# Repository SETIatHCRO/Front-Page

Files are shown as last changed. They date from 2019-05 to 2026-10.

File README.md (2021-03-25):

# ata_docs
Documentation related to the Allen Telescope Array at the Hat Creek Radio Observatory in Hat Creek, California

Contents:

[**Analog-Signal-Components:**](Analog-Signal-Components) Documents relating to analog signal components

*Librarian: Alexander Pollak*

[**Antenna:**](Antenna) Documents relating to Antenna geometry and optical design

*Librarian: Alexander Pollak*

[**Antonio-Feed:**](Antonio-Feed) Documents related to V2 Antonio Feeds

*Librarian: Alexander Pollak*

[**Beamformer:**](Beamformer) Documents related to the first ATA beamformer

*Librarian: Billy Barott*

[**EMI:**](EMI) Documents related to site and device electromagnetic interference (EMI/RFI)

*Librarian: Janusz Kulpa*

[**HCRO-Network-Infrastructure:**](HCRO-Network-Infrastructure) Documents and drawings related to the HCRO ethernet infrastructure 

*Librarian: Alexander Pollak*

[**HCRO-Time-Standard:**](HCRO-Time-Standard) Documents and drawings related to the 1pps and 10MHz time distribution.

*Librarian: Alexander Pollak*

[**HVAC-Signal-Processing-Room:**](HVAC-Signal-Processing-Room) Documents and drawings related to the HVAC upgrade.

*Librarian: Alexander Pollak*

[**SITE:**](SITE) Documents related to the HCRO Site

*Librarian: Jon Richards*

[**SonATA:**](SonATA) Documents related to the SETI on ATA (SonATA) System

*Librarian: Jon Richards*

[**NOTES:**](NOTES) The NOTES stored on tumulus. General operating procedures.

*Librarian: Jon Richards*

[**Network:**](Network) Documents and drawings related to network and computer access..

*Librarian: Jon Richards*

Go to the [-> head over to wiki](https://github.com/SETIatHCRO/ata_docs/wiki)

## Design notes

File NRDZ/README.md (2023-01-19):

This directory contains material and links for the NRDZ activities at HCRO.

[TARDyS4 Overleaf](https://www.overleaf.com/2563835296ydvcvszfkjnm)

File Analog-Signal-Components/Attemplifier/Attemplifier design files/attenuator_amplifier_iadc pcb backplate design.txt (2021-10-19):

FYI: https://webfiles.berkeley.edu/obm/public_html/digibee_plate2.pdf

---------------------------- Original Message ----------------------------
Subject: attenuator/amplifier/iadc  pcb backplate design
From:    "Oren Milgrome" <obm@berkeley.edu>
Date:    Tue, November 6, 2007 5:03 pm
To:      davidm@astro.berkeley.edu
         urry@astro.berkeley.edu
         melvyn.wright@gmail.com
         mdexter@calmail.berkeley.edu
Cc:      danw@milkyway.ssl.berkeley.edu
         hchen05@ssl.berkeley.edu
         welch@astro.berkeley.edu
         barottw@erau.edu
--------------------------------------------------------------------------

Hi, check out the quick sketch of a iBOB 2x2 channel ADC with 4 channel 6
bit attenuator/amplifier pcb backplate design:

https://webfiles.berkeley.edu/obm/public_html/digibee_plate2.pdf

We would connect the amplifiers to the ADCs with short cables and edge
mount sma connectors. The indvidual channels will be shielded with the
same can foil as the filter boards.

Sincerely, Oren
>
> I think extension idea is OK.
> I recommend we design the extension so as to avoid the upper and lower
> card guides.  I think the alignment for smooth install/remove would be
> too hard to get so maybe better to just avoid altogether.
> At first glance I don't think this imposes too many restrictions.
>
>
> On Tue, 6 Nov 2007, Oren Milgrome wrote:
>
>> Hi, I'll draw it up as a 4" plate extension holding a 3x?" 4 channel
>> attenplifer pcb. Is the length overhange ok? Looks like a plan.
>> Thanks, Oren
>> > Yep.
>> >
>> > Maybe having lots of spares would help in the sense that we could
>> > drill extra holes and such into "spare" plate and then just dismount
>> the
>> > iBob+2ADC from existing plate, mount to new super-plate and then
>> reinstall
>> > into chassis.  This would minimize the disruption at HCRO.
>> >
>> > Many spare plates are in the left filing cabinet in the office.
>> >
>> > Matt
>> >
>> > On Tue, 6 Nov 2007, Oren Milgrome wrote:
>> >
>> >> Hi, maybe we could make a extender for the back plate? We could add a
>> >> few
>> >> holes to the existing parts.
>> >> The 4 channel attenplifier pcb could mount to the extender plate, and
>> >> connect to ADC vis short smas? Regards, Oren
>> >>
>> >> > Oren,
>> >> >
>> >> > See attached.
>> >> > First round of ~10 boards were made by frontpanelexpress.com
>> >> > can download simple software to design and order.
>> >> >
>> >> > It's not that critical but for better or worse we do have a large
>> >> stock
>> >> > of  these plates.  probably have about 100 spare.
>> >> >
>> >> > Vendor: Protofab Inc.
>> >> >    Sheryl Eiberg
>> >> >    Assistant Project Manager
>> >> >    1310 Stub Road
>> >> >    Petaluma, CA 94954
>> >> >    707 782 9669
>> >> >
>> >> >                                                unit
>> >> > description                              QTY   price     price
>> >> >
>> >> > Digibee (iBob) aluminum plate            249  $19.21686  $4,785.00
>> >> > holes cut w/ water jet.
>> >> > then counter sunk on CNC machine.
>> >> >   9.1850" x 10.2750"
>> >> >   thickness 2.0 mm
>> >> >   corner radius 0.00"
>> >> >   material: aluminum
>> >> >   finish: alodine MIL-C-5541 Class 3
>> >> >   color: natural (clear to light yellow from alodine finish)
>> >> > 3 weeks.
>> >> >
>> >> >
>> >> > Matt
>> >> >
>> >> > On Tue, 6 Nov 2007, Oren Milgrome wrote:
>> >> >
>> >> >> Hi Matt, do you have any cad files or drawings for the IBOB/ADC
>> >> >> Backplates?
>> >> >> Maybe we could make new plates to hold the attenplifiers pcbs?
>> >> >>
>> >> >>
>> >> >>
>> >> >> --
>> >> >> Oren Milgrome
>> >> >> University of California - Berkeley
>> >> >> Radio Astronomy Lab 601 Campbell Hall
>> >> >> Berkeley, CA 94720-3411
>> >> >> mobile: 510 368 6857 office: 510 642 5509
>> >> >> lab: 510 642 0381 fax: 510 642 3411
>> >> >> email: obm@berkeley.edu
>> >> >>
>> >> >>
>> >>
>> >>
>> >> --
>> >> Oren Milgrome
>> >> University of California - Berkeley
>> >> Radio Astronomy Lab 601 Campbell Hall
>> >> Berkeley, CA 94720-3411
>> >> mobile: 510 368 6857 office: 510 642 5509
>> >> lab: 510 642 0381 fax: 510 642 3411
>> >> email: obm@berkeley.edu
>> >>
>> >>
>> >
>>
>>
>> --
>> Oren Milgrome
>> University of California - Berkeley
>> Radio Astronomy Lab 601 Campbell Hall
>> Berkeley, CA 94720-3411
>> mobile: 510 368 6857 office: 510 642 5509
>> lab: 510 642 0381 fax: 510 642 3411
>> email: obm@berkeley.edu
>>
>>
>

-- 
Oren Milgrome
University of California - Berkeley
Radio Astronomy Lab 601 Campbell Hall
Berkeley, CA 94720-3411
mobile: 510 368 6857 office: 510 642 5509
lab: 510 642 0381 fax: 510 642 3411
email: obm@berkeley.edu

-- 
Oren Milgrome
University of California - Berkeley
Radio Astronomy Lab 601 Campbell Hall
Berkeley, CA 94720-3411
mobile: 510 368 6857 office: 510 642 5509
lab: 510 642 0381 fax: 510 642 3411
email: obm@berkeley.edu

-- 
Oren Milgrome
University of California - Berkeley
Radio Astronomy Lab 601 Campbell Hall
Berkeley, CA 94720-3411
mobile: 510 368 6857 office: 510 642 5509
lab: 510 642 0381 fax: 510 642 3411
email: obm@berkeley.edu

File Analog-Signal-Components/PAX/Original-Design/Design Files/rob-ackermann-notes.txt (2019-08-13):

This is from an email dated October 01, 2009 by Rob Ackermann. It references images contained in this directory.

Jon Richards - August 13, 2019

**************

Attached PAX schematic image "pax-schematic.jpg" shows bits leaving microcontroller enter back attenuator shift-register at (A), leave at (B), and enter front attenuator shift-register at (C).  Also note that on/off bit (red circle) is associated with back attenuator shift-register.

Attached microcontroller source code image "set-pam-cmnd.png" shows first argument, back_atten, assigned to high byte of pam_data (green background highlight).  Second argument, front_atten, assigned to low byte of pam_data (blue background highlight).  On/off bit set in high byte, therefore, associated with back_atten (red background highlight).

Attached microcontroller source code image "set-pam-poll-data.png" shows setpam_data bits shifted from microcontroller to PAX shift-registers in order least significant bits (front attenuator) to most significant bits (yellow and orange background highlights).

Final image "pam-test-bench.jpg" shows PAM controller test bench setup with front and back attenuator bits represented by bar-graph LEDs

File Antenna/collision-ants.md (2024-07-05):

## <u> Collision Antennas </u>

### Background

The 3 collision trio antennas (3f, 3g, 3h) are located close enough to collide with each other given certain
orientations.  A JSDA service <i>CollisionServer</i> running on antcntl receives telemetry from these antennas
and judges whether each is should be allowed to move.

### Current Implementation

#### Drivebox motion enable/disable mechanism

The drivebox controls motor speeds through the Copley Accelnet servo amps by using the amp's velocity mode control.
The drivebox generates pulse trains for both az and el servo amps, and the amps translate this proportionally into the
desired motors speed.  The pulse train always has 50% duty cycle (it is not PWM).  These pulse trains are
generated by ip2022-based drivebox firmware's <i>TMR0</i> interrupt routine.

The drivebox firmware listens on <i>UDP</i> port 1519 for "pulse" packets, which is just a packet with the
payload >= 5 bytes containing `pulse` as those first 5 bytes.  With each pulse packet received, a counter is reset to 4,
and is decremented in the watchdog timer service routine which runs at 1 Hz.  The pulse train generator code returns
early when the counter value is > 0, effectively stopping pulse generation and thus motion immediately halts or cannot
started.  The implication of this is that should motion be judged externally by CollisionServer, the antenna may
continue to move for 3-4 seconds while the counter runs down.

There is only one "pulse" enable counter, and it controls both axes together.

#### Non-collision antenna behavior

For the non-collision antenna case, the controlbox continously sends the "pulse" UPD messages to the drivebox at 1 Hz,
so pulse-train generation and thus motion is always possible.

#### Telemetry and drive enable messaging

- `controlbox:encoder_thread()`:<br>Sends encoder readings at 10 Hz to `DishServer:Tracker:EncoderServer` at UDP localhost:1515

- `controlbox:wrappot_thread()`:<br>For collision ants, sends wrappot readings to `CollisionServer` at UDP antcntl:1515
at 1 Hz.  For non-collision ants, it sends `pulse` messages to the drivebox UDP port 1519 at 1 Hz.

- `EncoderServer:DatagramLoop()`:<br>Receives encoder reading messages on UDP port 1515

- `EncoderServer:azEncoderCollisionLoop()`:<br>Receives encoder reading messages on UDP port 1515, calculates az angle
and forwards az position to `CollisionServer` at UDP antcntl:1515

- `CollisionServer:RunReceiveThread()`:<br>Receives `wrappot` and `az` packets from the embedded EncoderServer on a
collision ant, processes and if judged ok, sends a `pulse` packet to that ant's controlbox UDP port 1517.

- `controlbox:drivebox_thread()`:<br>listens on UDP port 1517 for `pulse` messages from `CollisionServer`, essentially
forwarding them to the drivebox UDP port 1519.  

#### CollisionServer

<i>TODO</i>

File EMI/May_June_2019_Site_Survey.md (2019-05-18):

**A description of some proposed actions for site RFI/EMI Testing**

References:

NRAO Resources:

https://greenbankobservatory.org/science/gbt-observers/rfi-mitigation/

https://science.nrao.edu/facilities/vla/docs/manuals/obsguide/rfi

https://www.cv.nrao.edu/~hliszt/RFI/RFI.htm

https://science.nrao.edu/facilities/gbt/interference-protection/ipg

BRAND-EVN:

https://radiowiki.mpifr-bonn.mpg.de/lib/exe/fetch.php?media=jra:730562_radionet-del6.1_170630.pdf
(Appendix 1, Page 10)

Also see there test setup description at http://www1.oan.es/reports/doc/IT-CDT-2017-13.pdf and http://www1.oan.es/reports/doc/IT-CDT-2016-16.pdf

Report on anechoic chamber tests of a ROACH II (for discussion vis-a-vis Franklin’s report on LaserSETI)

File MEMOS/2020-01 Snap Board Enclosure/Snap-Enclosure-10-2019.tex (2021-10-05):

\documentclass[12pt,a4paper,oneside]{article}
\usepackage[margin=1.2in]{geometry}
\usepackage{appendix}
\usepackage[dvips]{graphicx}
\usepackage{epsfig}
\usepackage{amsmath}
\usepackage{amssymb}
\usepackage{psfrag}
\usepackage[square, comma,sort,numbers]{natbib}
\usepackage{fancyhdr}
\usepackage[nottoc]{tocbibind}
\usepackage{color}
\usepackage{fixltx2e}
\usepackage{pdfpages}
\usepackage{pdflscape}
\usepackage{booktabs}
\usepackage{graphicx}
\usepackage{float}
\usepackage{afterpage}
\usepackage{subcaption}
\usepackage{lscape}
\usepackage{rotating}
\usepackage{enumitem}
\usepackage{array,tabularx}
\usepackage{fancyref}
\usepackage[dvipsnames]{xcolor}
\usepackage[colorlinks=true,allcolors=blue]{hyperref}%

\newcommand{\quotes}[1]{``#1''}

\newenvironment{conditions*}
  {\par\vspace{\abovedisplayskip}\noindent
   \tabularx{\columnwidth}{>{$}l<{$} @{\ : } >{\raggedright\arraybackslash}X}}
  {\endtabularx\par\vspace{\belowdisplayskip}}

\pagestyle{fancy}
\title{\Huge Allen Telescope Array\\
\vspace{0.5cm}
Smart Network ADC Processor\\1U Enclosure\\
\vspace{0.5cm}
\normalsize \emph{}
\vspace{3.5cm}
\begin{center}
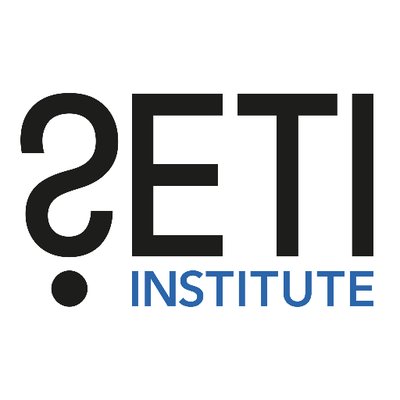
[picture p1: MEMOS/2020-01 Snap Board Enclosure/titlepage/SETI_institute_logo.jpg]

\end{center}
}
\author{ 
\vspace{1cm}
\Large
\textbf{ Alexander Pollak} \\
SETI Institute \\ 
189 Bernardo Ave, Suite 200 \\
Mountain View, CA 94043 \\ 
Alexander.Pollak.87@gmail.com\\
}
\date{\today}

\begin{document}
\clearpage\maketitle
\thispagestyle{empty}

%\newpage
%\thispagestyle{empty}
%\section*{Abstract}
%\noindent 
%

%
%\vspace{3cm}
%\begin{flushright}
%Alexander Pollak \\ \emph{September, 2015}
%\end{flushright}

%\newpage
%\thispagestyle{empty}
%\tableofcontents
\newpage

%----------------------------------------------------------------------------------------
%	SECTION 1
%----------------------------------------------------------------------------------------
%\pagestyle{plain}
\section{General}
\label{sec:1}
% ----------------------------------------------------------------

This document describes the design, component list, and assembly for a 1U SNAP Ver 2.1.1 MAR 2016 enclosure. The design is based on standard components and only requires two modified parts, which can be ordered via Front Panel Express using the included design files. In addition to housing the SNAP board, this design also includes SMA connections to support the ADC 5G V2.0 or any other compatible extension cards. Note, that this enclosure is not EMI-RFI shielded!

%----------------------------------------------------------------------------------------
\section{CAD Design and Drawings}
\label{sec:2}
% ----------------------------------------------------------------
This section includes a description of the CAD design. The enclosure has been designed to support all signal, communication, and power connections from the front. As a result of this, there was not enough space to include cooling fans into the front panel as well. In order to still ensure adequate cooling of the SNAP board and the 5G ADC card, directional fans have been installed which create an airflow from the right-hand side to the left-hand side. This configuration allows the 1U cases to be mounted without any space in between units while still providing sufficient cooling.

An image of the CAD model is shown in Figure \ref{fig:CAD-model}. One can see the internal arrangement of the SNAP board, power supply, directional fans, and the Raspberry Pi 2 Model B. The two custom parts are the front panel and the base plate, both colored in blue. The lid of the enclosure, not shown in this Figure, is perforated to further increase cooling. The drawings for the front panel and base plate are attached at the end of this document.

%
\begin{figure}[H]
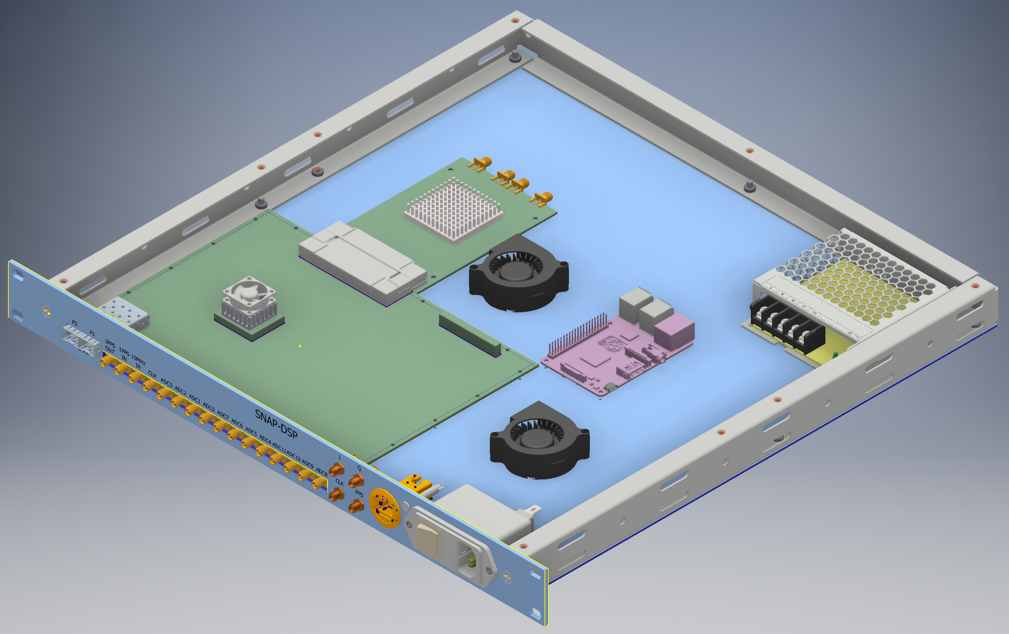
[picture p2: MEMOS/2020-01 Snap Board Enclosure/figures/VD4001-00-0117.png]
\centering{}
\caption{Schematic diagram of the measurement setup.}
\label{fig:CAD-model}
\end{figure}
%

\newpage

%----------------------------------------------------------------------------------------
\section{Component List}
\label{sec:3}
% ----------------------------------------------------------------
This section includes a list of the required components including their manufacturer and US distributer. The front panel and base plate can be ordered via {\color{blue} https://www.frontpanelexpress.com} by uploading the design files {\color{blue} VC4039-00-0001.fpd} and {\color{blue} VC4084-00-0018.fpd}. Not included are the SNAP board, 5G ADC card, and power supply cable from the PSU to the SNAP board. The total component cost for the enclosure is approximately 680\,USD.

\begin{table}[H]
\caption{Component List 1U SNAP Enclosure}
\resizebox{\textwidth}{!}{%
\begin{tabular}{@{}lllllll@{}}
\toprule
 Qty & Unit & Description                                              & Manufacturer             & PN Manufacturer & Distributor       & PN Distributer \\ \midrule
          &      &                                                          &                          &                             &                   &                             \\
1        & Each & LRS-75-12 -  POWER SUPPLY, AC-DC, 12V, 6A                	& Mean Well                		& LRS-75-12                   	& Newark            	& 44AC5561 \\
1        & Each & CHA-01-17, D-4001 1.75" Utility Chassis                  		& General Devices          		& CHA-01-17                   	& Quail Electronics 	& CHA-01-17 \\
1        & Each & Power Entry Module, Compact, IEC Inlet, 6A, 250VAC       	& SCHAFFNER                		& FN282-6-06                  	& Newark            	& 24M2150    \\
1        & Pack & Machine Screw, M3, 6 mm                                  			& TR FASTENINGS            	& M3 6 KRSTMC Z100	& Newark            	& 53M8781    \\
1        & Pack & SCREW, PAN HEAD PZ, M3, 4MM, 50PK                        	& DURATOOL                 		& DT000376                    	& Newark            	& 48AC6542  \\
1        & Pack & Machine Screw, M3, 25 mm                                 			& TRIPP-LITE         			& N001-S02-BL       		& Newark            	& 81Y0762  \\
1        & Each & Modular Connector, RJ45 Plug                             			& SCHNEIDER ELECTRIC       & XB5PRJ45                    	& Newark            	& 49AC2992  \\
1        & Each & Ethernet Cable, Cat5e, 600 mm, 2 ft                            		& SCHNEIDER ELECTRIC       & XB5PRJ45                    	& Newark            	& 49AC2992  \\
1        & Each & RPI2-MODB-V1.2                                           			& RASPBERRY-PI             	& RPI2-MODB-V1.2        	& Newark            	& 95Y1948    \\
1        & Each & GPIO Ribbon Cable for Raspberry Pi                       		& SAMTEC                   		& FFSD-20-D-04.00-01-N	& Newark            	& 99P5134    \\
1        & Each & ED Panel Mount Indicator, Green                          			& APEM                     		& Q6F3CXXG12E            	& Newark            	& 05W8310    \\
2        & Each & Fan Blower, GB Series, Compact, 12 V, DC                 		& SUNON                    		& GB1205PKV1-8AY.GN	& Newark            	& 96M8138     \\
18      & Each & SPACER, ROUND, POLYAMIDE, 4MM                           	& WURTH ELEKTRONIK         	& 960040010                  	& Newark            	& 94AC5835    \\
1        & Pack & SCREW, PAN HEAD PZ, M2, 8MM, 50PK                        	& DURATOOL                 		& DT000367                    	& Newark            	& 48AC6533      \\
1        & Pack & Washer, Plain, Brass, M2, Pack of 100                    		& DURATOOL                 		& M2 WASHER        		& Newark            	& 03P2386         \\
4        & Each & SMA Female to Female Adaptor Frequency: DC-6GHz          & Atlantic RF              		& SMA-1064 Rev A         	&                   &                             \\
4        & Each & Coaxial Cable Assemblies Standard Lengths - AFX Series   	& Atlantic RF              		& AFX-CA-141-24            	&                   &                             \\
1        & Each & Frontpanel                                               				& Front Panel Express, LLC 	& VC4039-00-0001.fpd     	&                   &                             \\
1        & Each & Base Plate                                               				& Front Panel Express, LLC 	& VC4084-00-0018.fpd    	&                   &                             \\
2        & Each & Fuse, Cartridge, Slow Blow, 2 A, 250 V                   		& Littlefuse               			& 0239002.HXP              	& Newark            	& 26K8412    \\
5        & Each & 8-32 X 3/8 STEEL ROUNDHEAD                               		& GC ELECTRONICS           	& KF-479                      	& Newark           	& 68R7355   \\
1        & Each & Barrier Terminal Block Connectors, Jumper, 38723 Series  	& MOLEX                    		& 38723-6502                  	& Newark            	& 72K2052    \\
7        & Each & Terminal, Locking, CLS Series, 22AWG to 18AWG, M3.5 	& MULTICOMP                		& CLS-TV-1806                 & Newark            	& 14T2409     \\ \bottomrule            
\end{tabular}}
\end{table}

%----------------------------------------------------------------------------------------
%	Power supply
%----------------------------------------------------------------------------------------
\section{Power Supply}
\label{sec:5}
% ----------------------------------------------------------------

The SNAP FPGA board and the cooling fans are supplied with a Mean Well 75\,W switch-mode PSU.
The unit is mounted directly to the base plate of the enclosure, thereby using the case as a thermal heatsink.
The operating temperature range of the PSU is from $-30^{\circ}$C through $70^{\circ}$C and the technical specifications are shown in Table \ref{tab:psu_spec}.
The power entry module, mounted in the front panel, combines an IEC inlet and a mains filter with a dual-fuse holder. The AC supply fuse current rating for this unit is selected to be 2\,A. 

\begin{table}[H]
\centering
\caption{Power Supply Specification}
\label{tab:psu_spec}
\begin{tabular}{@{}ccccc@{}}
\toprule
\multicolumn{1}{l}{Description} & \multicolumn{1}{l}{Output Voltage} & \multicolumn{1}{l}{Output Current} & \multicolumn{1}{l}{Power W} & \multicolumn{1}{l}{Input Voltage} \\ \midrule
LRS-75-12                         & 12\,VDC                               & 6A                               & 75W                         & $85 \sim 264\,\rm{VAC}$                              \\ \bottomrule
\end{tabular}
\end{table}

%----------------------------------------------------------------------------------------
%	Assembly
%----------------------------------------------------------------------------------------
\section{Assembled Unit}
\label{sec:6}
% ----------------------------------------------------------------
\begin{figure}[H]
\centering
   \begin{subfigure}[b]{1\textwidth}
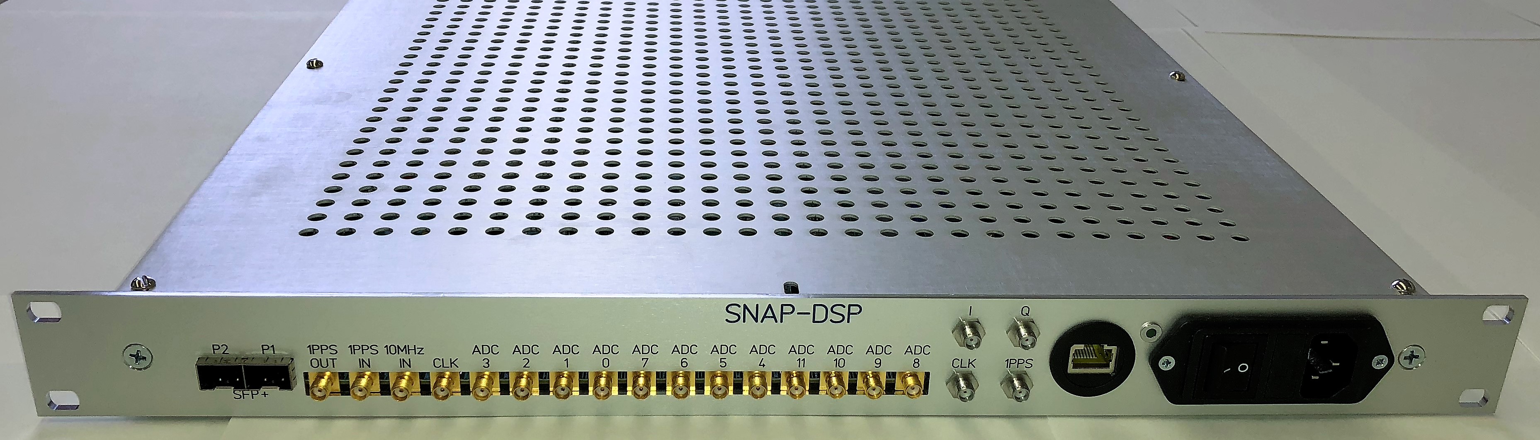
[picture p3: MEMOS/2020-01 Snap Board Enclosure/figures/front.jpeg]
   
   \caption{}
   \label{fig:front-view} 
\end{subfigure}
\begin{subfigure}[b]{1\textwidth}
	\vspace{1cm}
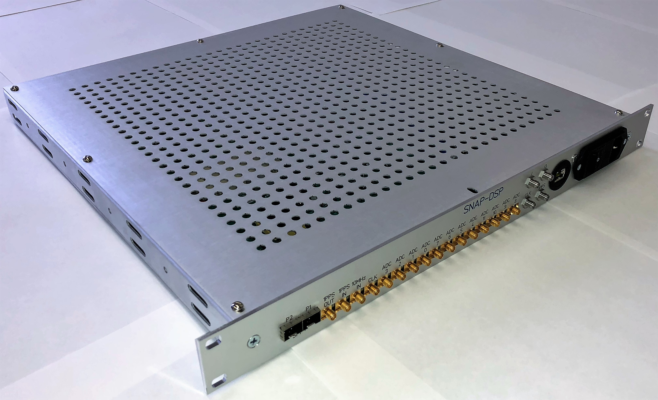
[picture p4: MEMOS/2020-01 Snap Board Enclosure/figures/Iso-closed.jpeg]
   
   \caption{}
   \label{fig:iso-view}
\end{subfigure}
\caption[Three numerical solutions]{Assembled 1U SNAP Enclosure; (a) Front view (b) Iso view.}
\label{fig:assembled-unit}
\end{figure}

%
\begin{figure}[H]
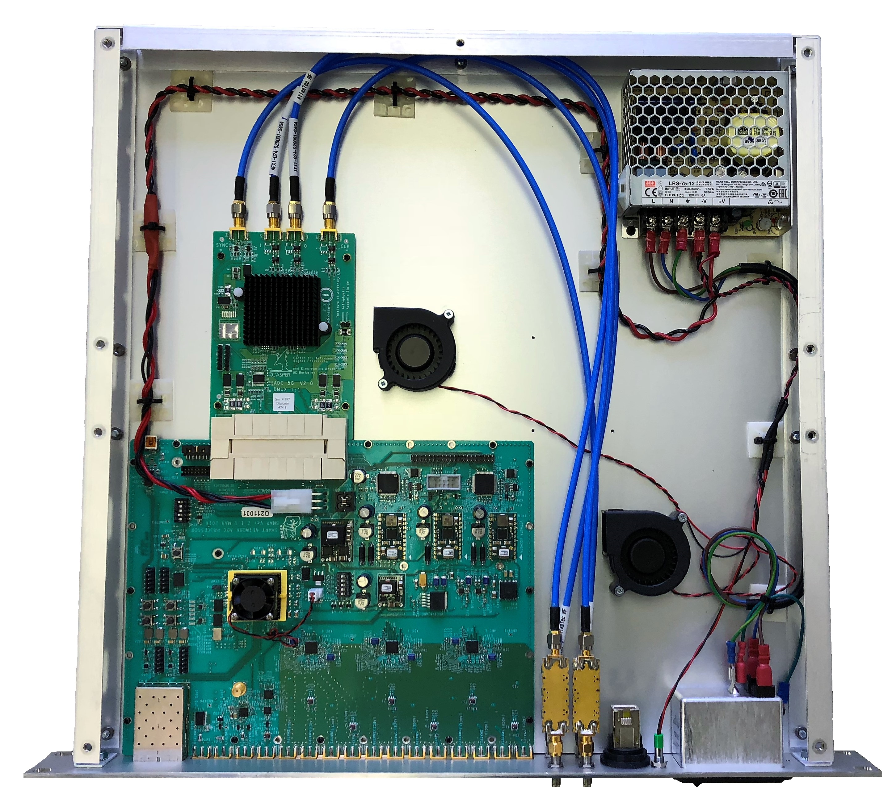
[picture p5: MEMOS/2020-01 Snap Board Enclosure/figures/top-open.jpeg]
\centering{}
\caption{Top view of the assembled case with the lid removed. Note that this unit has no Raspberry Pi installed.}
\label{fig:CAD-model}
\end{figure}
%

%----------------------------------------------------------------------------------------
%	APPENDIX
%----------------------------------------------------------------------------------------

\includepdf[pages={-},fitpaper,rotateoversize]{figures/VC4039-00-0001.pdf}
\label{DRAWING:VC4039-00-0001}
\includepdf[pages={-}, fitpaper,rotateoversize]{figures/VC4084-00-0018.pdf}
\label{DRAWING:VC4084-00-0018}

%----------------------------------------------------------------------------------------
%	BIBLIOGRAPHY
%----------------------------------------------------------------------------------------

%\bibliographystyle{apalike}
%\bibliographystyle{abbrv}

\bibliographystyle{apsrev}
\bibliography{bib_memos}

%----------------------------------------------------------------------------------------

\end{document}

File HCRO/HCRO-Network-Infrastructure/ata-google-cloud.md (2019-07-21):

ATA Data Google Cloud Storage
Jon Richards
SETI Institute
June 25, 2019

Introduction

This document explains details of the Google Cloud Storage used for ATA data. This includes the SQL database instance.

If you have any access issues, need access to the data buckets, etc., contact Jon Richards (jrichards@seti.org) and he will give you any access you want. You may wish to contact him first to make sure you should have access, before you get confused in the installation steps below.

For data storage the cloud is accessed using the gsutil utility provided by Google. There is a list of available commands:

•	Go to: https://cloud.google.com/storage/docs/gsutil_install
•	In the menu on the left igrate to gsutil tool -> gsutil Commands

Data Storage Bucket

The ATA data storage is located under the SETI-ATA Cloud project. The project name is “probable-cove-796”. It is in a bucket called ata_data. You access the files with the path “gs://ata_test_data”, once you have successfully completed “gcloud config” described below.

To view all the data directories in the probable-cove-796 project go to:

•	https://console.cloud.google.com/storage/browser/ata_test_data?project=probable-cove-796

The ata_test_data directory is under there; you can click to view all the files. 

Currently, the following ATA computers have access to this data configured and working, under the jrseti@gmail account:

•	NSG-head – this is the head node where the on/off data is stored in the /data directory.
•	sonata1 – this is the computer that contains the database and various utilities. The database on this computer is eventually going to be migrated to the cloud.
•	chan1x – this computer is used to read data from the beamformer, usually beam 1, x pol, and store it on a large disk mounted as “/data”. Relating to the cloud, the usual use case for this computer is to read and store beamformer data as it streams in (using hashpipe), convert the data to filterbank format, and push this data in the cloud. It is possible that some raw beamformer data  may be moved to the cloud, but it is so large and oppressive that hopefully storing raw beamformer data in the cloud will be a rare case.
•	chan2x – Same as “chan1x”, but for another beam or pol

SQL Database Instance

The SQL database instance stores all the feed sensor data. Grafana uses this instance as a data source. In theory anyone should be able to run his or her own Grafana server and use this SQL database instance as a data source.

The SQL database instance is at: 34.83.6.3, the database name is “ants”

To access read only, should work for anyone from any computer:

•	mysql --host=34.83.6.3--user=ata-sensors ants

Read/Write access is available if you connect from any computer originating from the ip address of the ATA, 70.100.31.22. Also, the user must be “ata-sensors-rw”.

•	mysql --host=34.83.6.3 --user=ata-sensors-rw ants

Utilities Installation
 
On your computer you need to do the following to access the data. Note that you will be using your own 

Install gsutil, follow the instructions at:

•	 https://cloud.google.com/storage/docs/gsutil_install

Once gsutil is installed, init your access to the gloud:

•	gcloud auth login --no-launch-browser (then follow directions)

Tell your computer which data bucket to use:

•	gcloud config set project probable-cove-796

You should now be able to access the data. Test that you can read a file from the gs://ata_data directory. There is a test file just for this purpose:

•	gsutil cp gs://ata_test_data/access_test_file.txt
•	Verify that access_test_file.txt transferred to your computer and you can view the simple text contents of the file.

Test your ability to write to the data directory, if you have write permissions. It may be the case you do not have write permissions if your use case is just to read data files. It is assumed that most users will not need or want write access, but if that is the case for you, test:

•	On your computer create a dummy file: “touch my_test.dat”
•	gsutil cp my_test.dat gs://ata_test_data
•	Go to https://console.cloud.google.com/storage/browser/ata_test_data?project=probable-cove-796
•	
•	View the list of files. You should see “my_test.dat” in the list. You may need to perform a refresh in your browser to see the data.
•	Remove the file: gsutil r mgs://ata_test_data/my_test.dat. Refresh the browser and confirm the file is removed.

Examples:

Rsync 6GB of files from /data/20190625 on NSG-head to gs://ata_test_data/rfi/:  

•	Do this in a screen!
•	cd /data
•	gsutil rsync -r 20190625 gs://ata

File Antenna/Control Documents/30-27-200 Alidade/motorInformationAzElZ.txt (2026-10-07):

Motor information:

PO#:12734.02PD 09/01/2005 [Incomplete] Cymatix MINEX
   011003: $53,909.00
	01	Qty: 47 ea  Az/El motor 
		"Part #AKM42J-EKMN2-03, Servo motor, 160VDC, 31.5 in-lb, 8.4 amp, 
		customized for IP20 plugs flying leads with J winding, 
		Housing 3.307 x 3.307 x 5.82, boss 2.875 x 0.118, pattern 0.218 on 3.875 circle, 
		shaft 0.500 x 1.250, key 0.125 x 0.750," 
		$475.00 /ea, $22,325.00 total

	02	Qty: 94 ea Az/El servo amplifier
		"Part #ACM-180-20-module, Servo amplifier, Accelnet module.180 VDC, 
		10 amp continuous, 20 amp peak." 
		$336.00 /ea $31,584.00 total
---------------------------------------------------------------------------------
(005:478) PO#:12774.03PD 09/01/2005 [Incomplete] Cymatix MINEX
   011003: $20,840.00
	01	Qty: 47 ea feed drive motor
		"Part #SN32HRYY-LNK-NS-00, Motor, AC Synchronous, Pacific Scientific, 
		NEMA 34, 3.38""sqr x 4.64 lg, 0.500""dia x 1.25""lg, 72 rpm, 480 0z-in running, 
		120VAC, 60 Hz, 1 Ph, flying leads (note: requires Resistor 200 ohm, 50w & requires Capacitor, 
		10uf x 370 Vac)" 
		$262.00 /ea $12,314.00 total

AKM42J-EKMN2-03
"AKM": AKM series
"4"  : motor frame size 4
"2"  : rotor stack length 2
"J"  : winding type J
"E"  : NEMA mount
"K"  : open keyway
"M"  : 0.5m shielded cable with IP20 plugs
"N"  : no brake
"2"  : 2048 PPR digital encoder w/ commutation
"03" : special shaft seal 03

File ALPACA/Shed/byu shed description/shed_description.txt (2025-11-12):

The sheds interior dimensions are 10' x 10' with an additional 4'3" x 2'5" x
5'10" nook in the back right corner for the comporessor. The interior floor to
ceiling dimension of BYU's shed is 8'.

ALPACA's dimenions when in the cart are described in:
'alpaca-cart-dimensions.png', 'ALPACA-clearnances.pdf', 'ALPACA-forklift
clearance.pdf'

The included drawings in, `ShedDrawings_July_2020.pdf` detail the shed's
construction, dimenions, and electrical specificaiton on pgs. 4-5. 

There are a few discrepancies from that drawing and what was built. It is best
to consider that document as a reference and what the building mateiral
specifications were. The signficant differences worth noting are:

  - The door is not center to the shed entrance. The door frame starts 18 inches
from the left and 36 inches from the right. This was to allow us to clear
the fenced area on BYU's roof and use the full range of motion in the cart to
tilt the array to the horizontal. This is shown in 'shed-door-dimensions.png'

  - A 4'3" x 2'5" x 5'10" nook for the comporessor in the back right corner.
The initial drawing shows the compressor outdoors, and did not include the
nook in the shed for the compressor. The space for the compressor was added
during construction of the shed with the change to instead store and run the
compressor from within the shed. We move the helium cables as needed when moving
the instrument in and out of the shed. Dimenions of this nook in the current
shed are shown in 'compressor_location.jpg'. A view of the compressor from the
outside is shown in "shed_side_compressor.jpeg" and
"shed_side_compressor_closed.jpeg".

Other current shed informaiton:

Door height has a clearance of 85" (shown in 'shed-door-dimensions.png')

The shed is insulated.

Included pictures show the rail dimensions and spacing as currently installed.
These rails we can remove from and ship with the instrument. Rails are shown in
'rails.jpeg'.

There are quad duplex NEMA 5-20R 120V outlet assemblies on each wall. The outlets are
4' off the ground on the back and side walls. The outlet on the 36" wall with the
door is 2' off the ground. We have four 20 A 120V circuits on our panel.

One 60A 480V 3 phase circuit for the compressor. The compressor is rated to
operate at 20A. More details about electrical operation of the compressor are in
the 'trillium-m700rt-helium-compressor-manual-c.pdf' on page 6.

Changes for at ATA:

- Increase the internal ceiling to floor height to at least 9' x 6". A 10'
  ceiling would add comfortable margin. This allows for replacing/removal of the
  top hat and servicing the array without taking the array outside. 

- Increase the door height by at least 3 inches

- Extend the shed to at least 2 to 3 feet in each dimension. As seen in the
  photos, there is enough room to work, but it is cramped. We also cannot
  service the instrument at the horizontal. Increasing the ceiling height and
  length will provide more space to conveniently service the array.

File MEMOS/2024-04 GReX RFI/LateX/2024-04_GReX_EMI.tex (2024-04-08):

\documentclass[12pt,a4paper,oneside]{article}
\usepackage[margin=1.2in]{geometry}
\usepackage{appendix}
\usepackage[dvips]{graphicx}
\usepackage{epsfig}
\usepackage{amsmath}
\usepackage{amssymb}
\usepackage{psfrag}
\usepackage[square, comma,sort,numbers]{natbib}
\usepackage{fancyhdr}
\usepackage[nottoc]{tocbibind}
\usepackage{color}
\usepackage{fixltx2e}
\usepackage{pdfpages}
\usepackage{pdflscape}
\usepackage{booktabs}
\usepackage{graphicx}
\usepackage{float}
\usepackage{afterpage}
\usepackage{subcaption}
\usepackage{lscape}
\usepackage{rotating}
\usepackage{enumitem}
\usepackage{array,tabularx}
\usepackage{fancyref}
%\usepackage[dvipsnames]{xcolor}
\usepackage[colorlinks=true,allcolors=blue]{hyperref}%
\usepackage[table,xcdraw]{xcolor}

\newcommand{\quotes}[1]{``#1''}

\newenvironment{conditions*}
  {\par\vspace{\abovedisplayskip}\noindent
   \tabularx{\columnwidth}{>{$}l<{$} @{\ : } >{\raggedright\arraybackslash}X}}
  {\endtabularx\par\vspace{\belowdisplayskip}}

\pagestyle{fancy}
\title{\Huge The Hat Creek Radio Observatory\\
\vspace{0.5cm}
GReX Electromagnetic Interference Measurements\\
\vspace{0.5cm}
\normalsize \emph{}
\vspace{3.5cm}
\begin{center}

\end{center}
}
\author{ 
\vspace{1cm}
\Large
\textbf{Alexander Pollak, Wael Farah, Marc Jacquart} \\
SETI Institute \\ 
339 Bernardo Ave, Suite 200 \\
Mountain View, CA 94043 \\ 
Alexander.Pollak.87@gmail.com\\
}
\date{\today}

\begin{document}
\clearpage\maketitle
\thispagestyle{empty}

\newpage

%----------------------------------------------------------------------------------------
%	General
%----------------------------------------------------------------------------------------

This document summarizes the testing of the GReX electronics' EM interferences at the Hat Creek Radio Observatory (HCRO) on April 3rd, 2024.

\section{Measurement setup}
\label{sec:Testing}

The GReX unit is place in the HCRO's screened room and it's electromagnetic emissions are recorded by a spectrum analyzer connected to an omnidirectional antenna through a signal amplifier. A schematic of the setup is shown in figure \ref{fig:measurement_setup_schematics}, a list of the components used in table \ref{tab:setup_component_list} and a picture of the setup inside the screened room is shown in figure \ref{fig:screened_room_setup}. A list of settings for the spectrum analyzer is shown in table \ref{tab:spectrum_analyzer_settings}. One modification was done for all the tests, compared to the state in which the GReX module was received: steel wool was added in the opening for the fiber cable to further shield the GReX enclosure.

A first baseline measurement was done with all the GReX electronics turned off. Then, the GReX was powered on and the emission spectrum was recorded for the GReX enclosure closed and opened separately. The SNAP board was programmed with the ``2023-08-16\_1325'' firmware after switching the unit on, but the 10 Gigabit Ethernet output was not enabled. As a final test, RF absorbers were placed in the GReX enclosure and the emission spectrum was once again measured with the enclosure closed. The hypothesis tested here is that the GReX enclosure acts as a resonant chamber for the EMI. Adding absorbers in the enclosure would reduce the interferences inside the enclosure, thus reducing the amount escaping the enclosure causing interferences on the outside.

\begin{figure}[H]
\centering
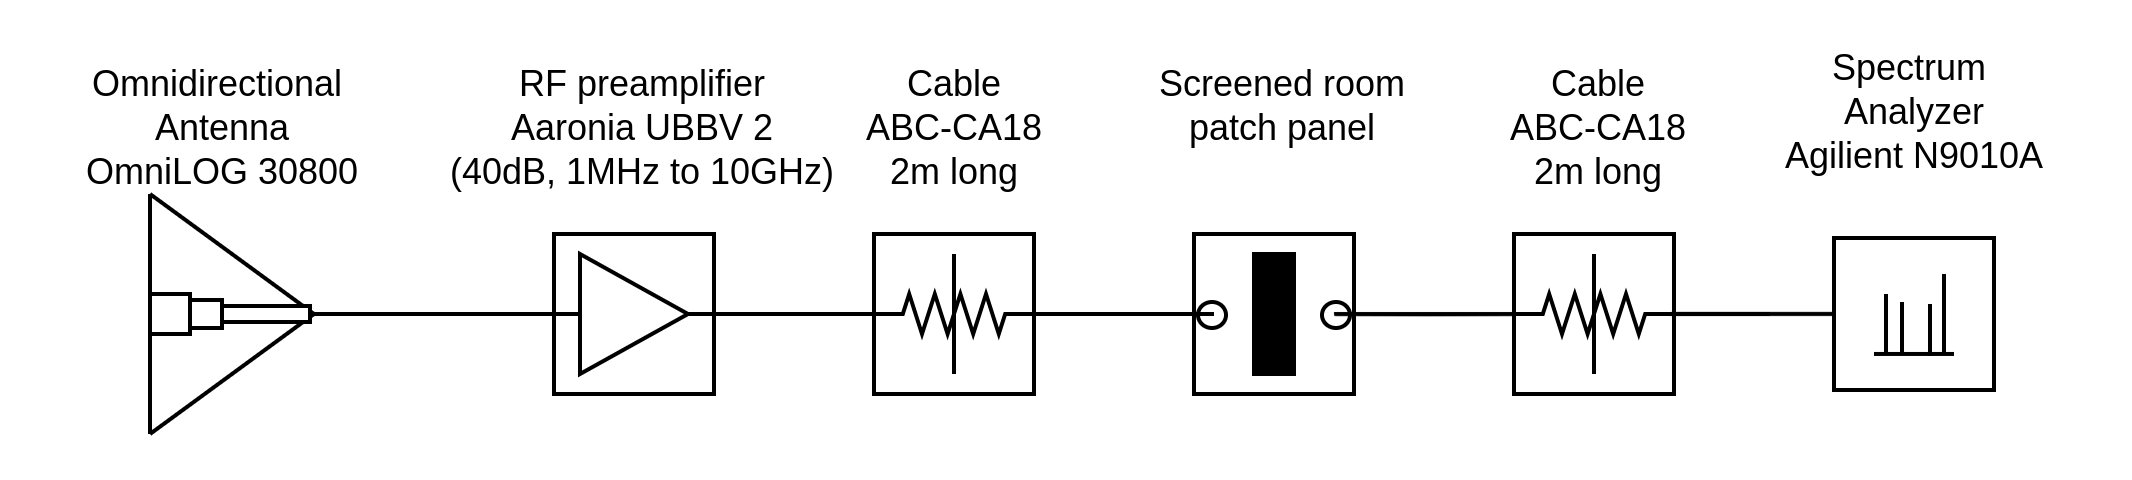
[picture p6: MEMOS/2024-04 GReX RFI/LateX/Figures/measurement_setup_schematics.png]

\caption{GReX EMI measurement setup schematics.}
\label{fig:measurement_setup_schematics}
\end{figure}
%
\begin{figure}[H]
\centering
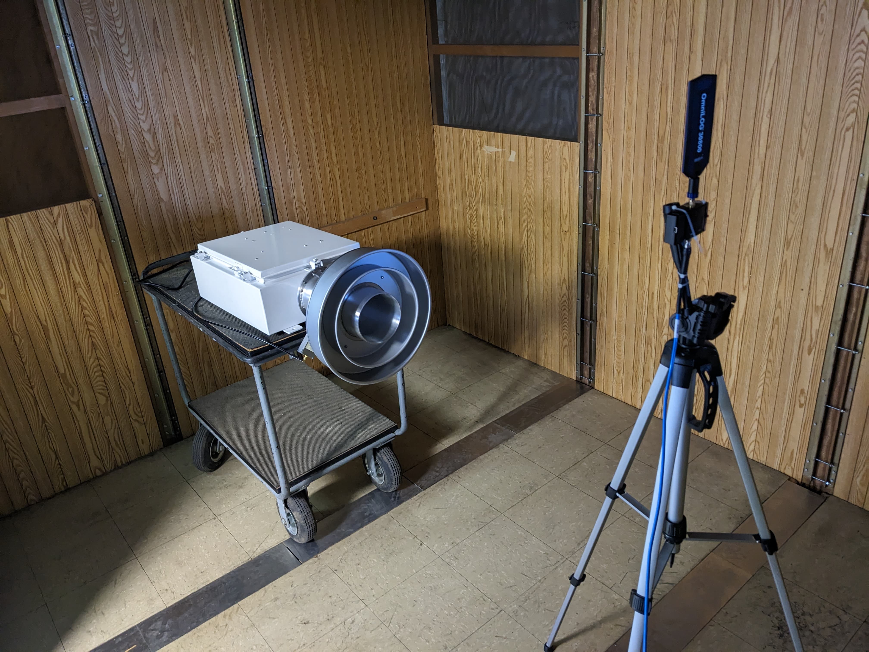
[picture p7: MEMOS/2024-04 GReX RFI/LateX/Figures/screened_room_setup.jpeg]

\caption{GReX EMI measurement setup in the HCRO screened room.}
\label{fig:screened_room_setup}
\end{figure}
%
\begin{table}[]
    \centering
   
    \begin{tabular}{|c|c|}
    \hline
         \cellcolor[gray]{0.85} Description & \cellcolor[gray]{0.85} Designation \\ \hline
         Omnidirectional antenna & OmniLOG 30800\\ \hline
         RF preamplifier & Aaronia UBBV 2\\ \hline
         Female-Female SMA cable 2m & ABC-CA18-SMSM-2.OM\\ \hline
         Female-Female SMA cable 5m & ABC-CA18-SMSM-5.OM\\ \hline
         Spectrum analyzer & Agilent N9010A\\ \hline
    \end{tabular}
    \caption{Components list for the GReX EMI measurements.}
    \label{tab:setup_component_list}
\end{table}

\begin{table}[]
    \centering
   
    \begin{tabular}{|c|c|}
    \hline
         \cellcolor[gray]{0.85} Description & \cellcolor[gray]{0.85} Setting \\ \hline
          Start Frequency & $300\thinspace$MHz \\ \hline
          Stop Frequency & $6\thinspace$GHz \\ \hline
          Number of points & 1001 \\ \hline
          Sweep time & 656.176 s\\ \hline
          RBW & $100\thinspace$Hz \\ \hline
          VBW & $1000\thinspace$Hz \\ \hline
          Attenuation & 0 dB\\ \hline
          Trace type & Maxhold \\ \hline
          Detector & Peak \\ \hline         
    \end{tabular}
    \caption{ Agilent N9010A specrum analyzer settings list for the GReX EMI measurements.}
    \label{tab:spectrum_analyzer_settings}
\end{table}
% ----------------------------------------------------------------
\section{Results}
\label{sec:Results}

The baseline spectrum is shown in figure \ref{fig:baseline_result}. The emission peaks around $1\thinspace$GHz are due to the EMI emitted by the spectrum analyzer itself, even though it is set outside the screened room for the measurements. However, this contribution is negligible compared to the GReX measurements shown below. Figure \ref{fig:open_result} shows the spectrum for the GReX enclosure open. The spectrum measurement result with the GReX enclosure closed is shown in figure \ref{fig:closed_result}. Finally, figure \ref{fig:absorber_comparison_spectrum} shows the effect of adding absorbers inside the enclosure. These four spectra are respectively referred below as ``baseline'', ``open'', ``closed'' and ``absorber''. A list of the highest interference peaks, defined as a value greater than $30\thinspace$dB above its neighbors and a distance of at least 5 spectrum values between each peaks, is reported in table \ref{tab:main_emission_peaks}.

\begin{figure}[H]
\centering
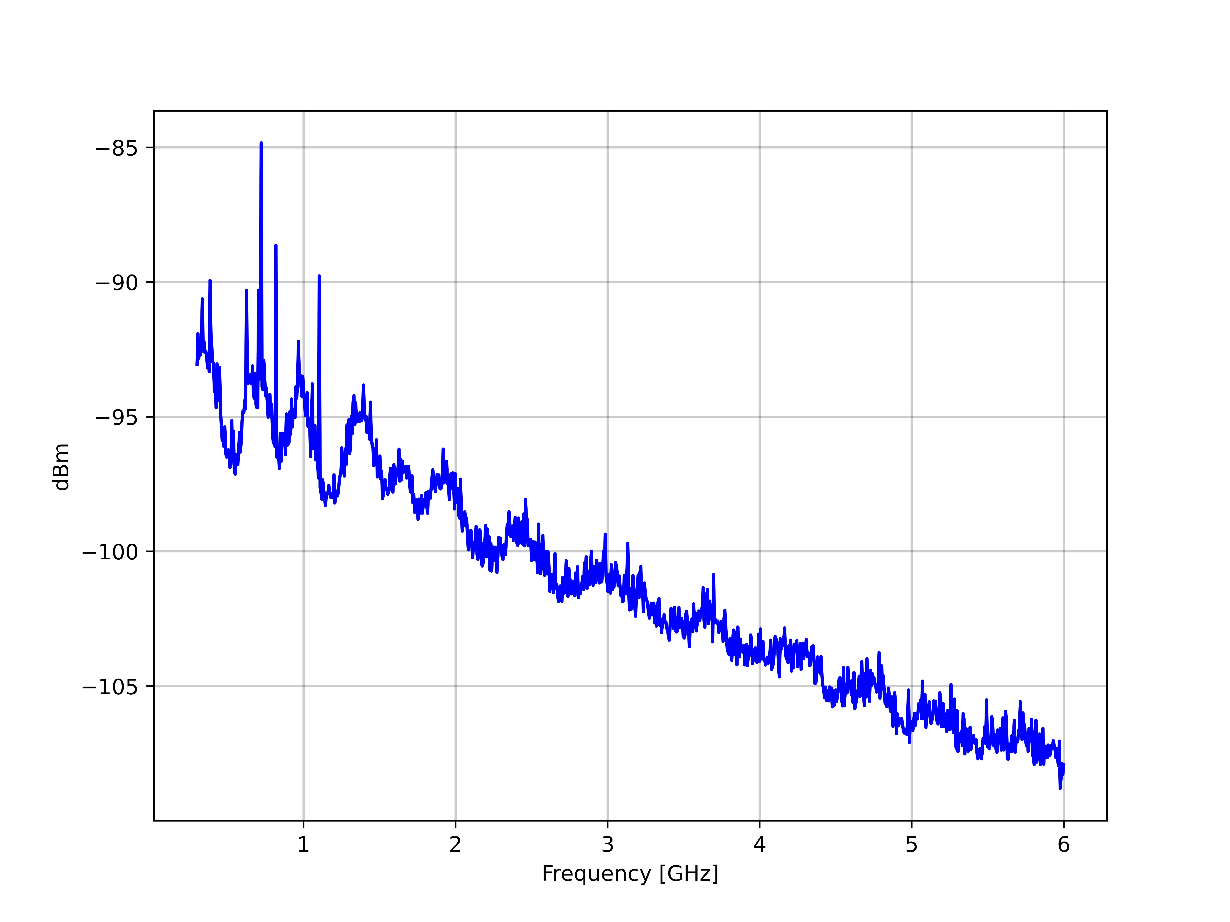
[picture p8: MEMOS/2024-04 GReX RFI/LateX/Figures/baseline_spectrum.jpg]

\caption{Baseline spectrum for the GReX EMI measurements.}
\label{fig:baseline_result}
\end{figure}
%
\begin{figure}[H]
\centering
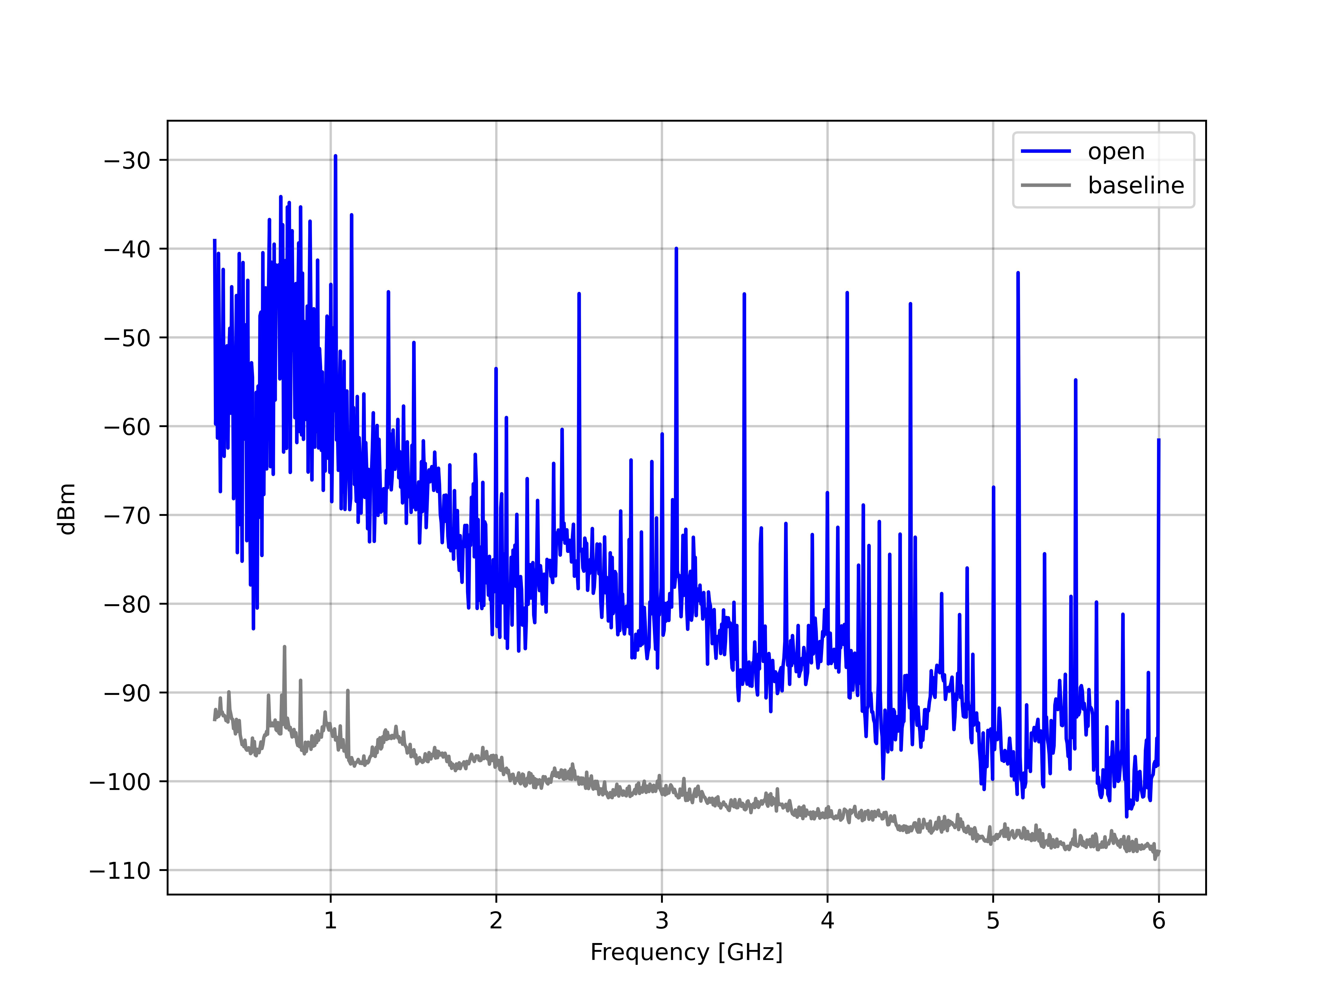
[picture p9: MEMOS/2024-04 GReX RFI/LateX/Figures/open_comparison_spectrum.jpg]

\caption{EMI emission spectrum of the GReX unit with its enclosure opened, compared with the baseline spectrum.}
\label{fig:open_result}
\end{figure}
%
\begin{figure}[H]
\centering
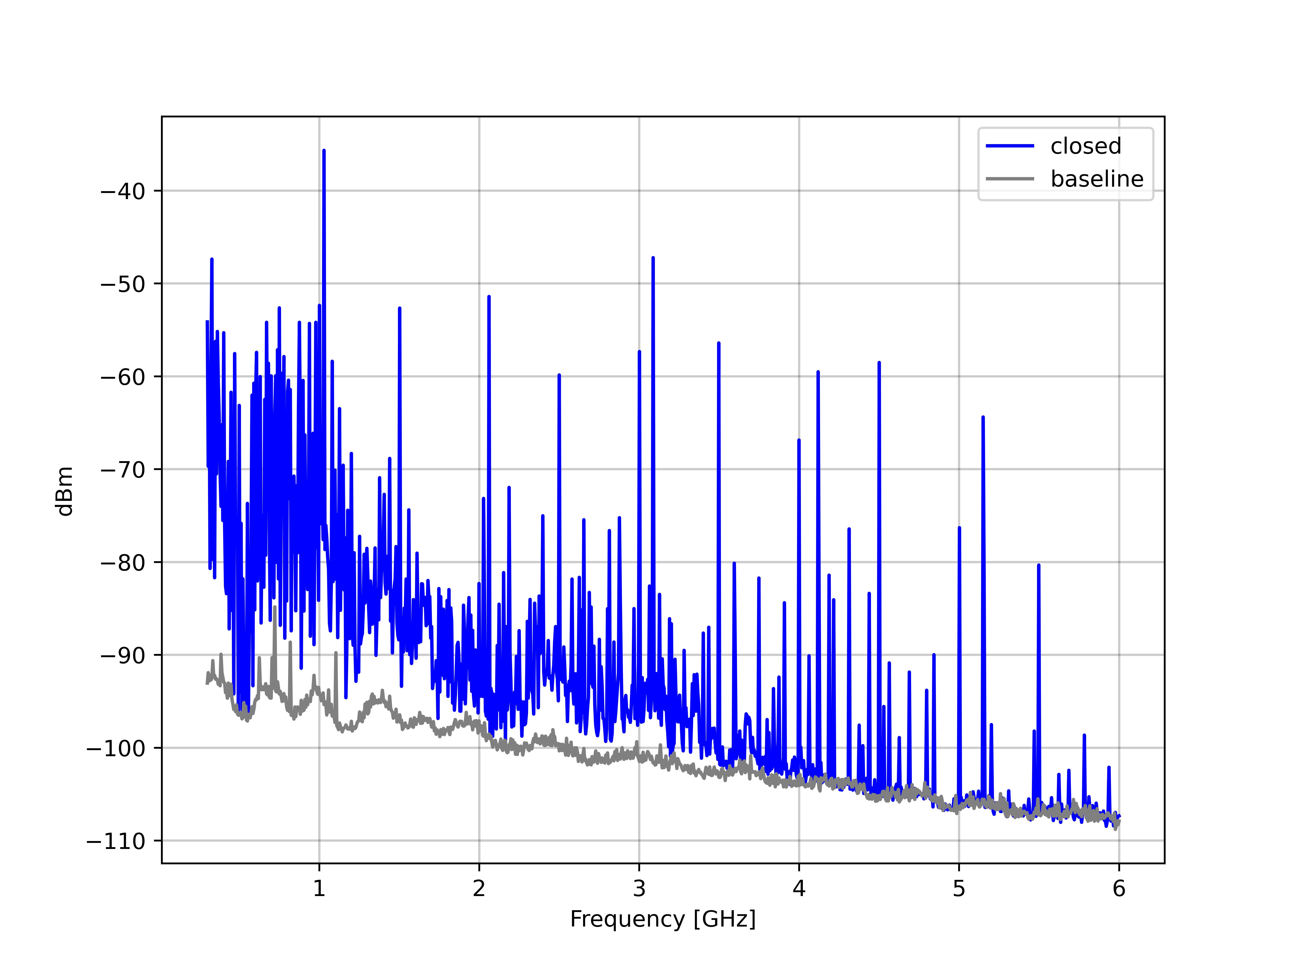
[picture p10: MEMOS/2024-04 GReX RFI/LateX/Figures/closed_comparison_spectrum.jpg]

\caption{EMI emission spectrum of the GReX unit with its enclosure closed, compared with the baseline spectrum.}
\label{fig:closed_result}
\end{figure}
%
\begin{figure}[H]
\centering
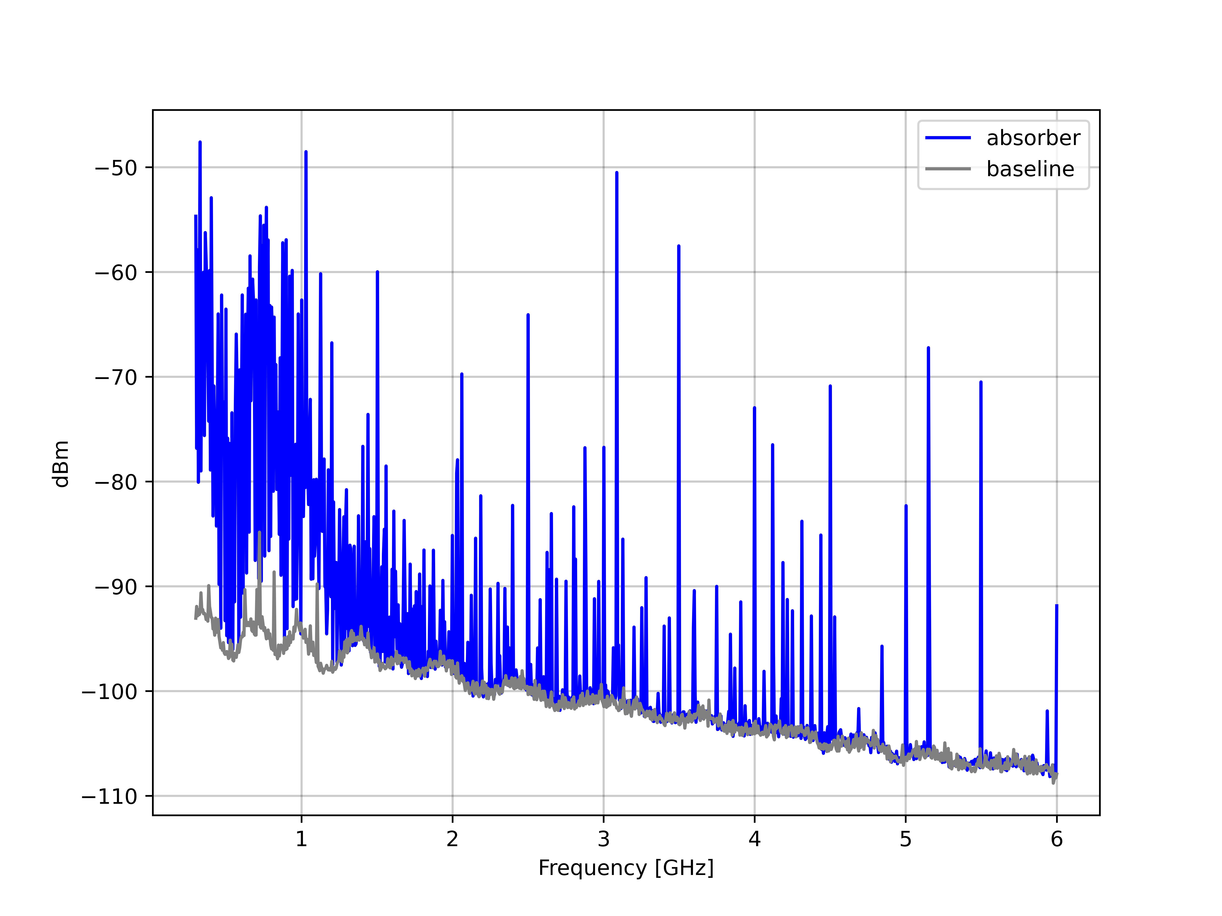
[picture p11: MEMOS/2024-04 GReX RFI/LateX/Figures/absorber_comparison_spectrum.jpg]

\caption{EMI emission spectrum of the GReX unit with its enclosure closed and absorbers added inside the enclosure, compared with the baseline spectrum.}
\label{fig:absorber_comparison_spectrum}
\end{figure}

\begin{table}[]
    \centering
   
    \begin{tabular}{|c|c|c|}
    \hline
         \cellcolor[gray]{0.85} Measurement & \cellcolor[gray]{0.85} Frequency [GHz] &  \cellcolor[gray]{0.85} Amplitude [dBm]\\ \hline
         open & 3.0873 & -39.978501 \\ \hline
         open & 3.4977 & -45.107806 \\ \hline
         open & 4.1190 & -44.959350 \\ \hline
         open & 4.5009 & -46.206643 \\ \hline
         open & 5.4984 & -54.792139 \\ \hline
         \hline
         closed & 0.4995 & -63.143009 \\ \hline
         closed & 1.0296 & -35.672183 \\ \hline
         closed & 1.5027 & -52.661033 \\ \hline
         closed & 2.0613 & -51.418850 \\ \hline
         closed & 2.5002 & -59.862832 \\ \hline
         closed & 3.0018 & -57.345924 \\ \hline
         closed & 3.0873 & -47.234282 \\ \hline
         closed & 3.4977 & -56.419926 \\ \hline
         closed & 3.9993 & -66.870435 \\ \hline
         closed & 4.5009 & -58.519204 \\ \hline
         \hline
         absorber & 1.0296 & -48.517166 \\ \hline
         absorber & 2.5002 & -64.079893 \\ \hline
         absorber & 3.0873 & -50.503989 \\ \hline
         absorber & 3.4977 & -57.511396 \\ \hline
         absorber & 3.9993 & -72.956611 \\ \hline
         absorber & 4.5009 & -70.879781 \\ \hline
         absorber & 5.4984 & -70.499525 \\ \hline

    \end{tabular}
    \caption{List of main emission peaks in the spectrum recorded for the GReX EMI measurements. Computed using scipy.signal's find\_peaks function (threshold: 30, distance: 5).}
    \label{tab:main_emission_peaks}
\end{table}

\end{document}

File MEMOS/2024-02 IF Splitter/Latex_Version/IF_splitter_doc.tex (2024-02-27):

\documentclass[12pt,a4paper,oneside]{article}
\usepackage[margin=1.2in]{geometry}
\usepackage{appendix}
\usepackage[dvips]{graphicx}
\usepackage{epsfig}
\usepackage{amsmath}
\usepackage{amssymb}
\usepackage{psfrag}
\usepackage[square, comma,sort,numbers]{natbib}
\usepackage{fancyhdr}
\usepackage[nottoc]{tocbibind}
\usepackage{color}
\usepackage{fixltx2e}
\usepackage{pdfpages}
\usepackage{pdflscape}
\usepackage{booktabs}
\usepackage{graphicx}
\usepackage{float}
\usepackage{afterpage}
\usepackage{subcaption}
\usepackage{lscape}
\usepackage{rotating}
\usepackage{enumitem}
\usepackage{array,tabularx}
\usepackage{fancyref}
\usepackage[dvipsnames]{xcolor}
\usepackage[colorlinks=true,allcolors=blue]{hyperref}%

\newcommand{\quotes}[1]{``#1''}

\newenvironment{conditions*}
  {\par\vspace{\abovedisplayskip}\noindent
   \tabularx{\columnwidth}{>{$}l<{$} @{\ : } >{\raggedright\arraybackslash}X}}
  {\endtabularx\par\vspace{\belowdisplayskip}}

\pagestyle{fancy}
\title{\Huge The Hat Creek Radio Observatory\\
\vspace{0.5cm}
The IF Splitter\\
\vspace{0.5cm}
\normalsize \emph{}
\vspace{3.5cm}
\begin{center}

\end{center}
}
\author{ 
\vspace{1cm}
\Large
\textbf{ Alexander Pollak \& Marc Jacquart} \\
SETI Institute \\ 
339 Bernardo Ave, Suite 200 \\
Mountain View, CA 94043 \\ 
Alexander.Pollak.87@gmail.com\\
}
\date{\today}

\begin{document}
\clearpage\maketitle
\thispagestyle{empty}

%\newpage
%\thispagestyle{empty}
%\section*{Abstract}
%\noindent 
%

%
%\vspace{3cm}
%\begin{flushright}
%Alexander Pollak \\ \emph{September, 2015}
%\end{flushright}

%\newpage
%\thispagestyle{empty}
%\tableofcontents
\newpage

%----------------------------------------------------------------------------------------
%	General
%----------------------------------------------------------------------------------------
%\pagestyle{plain}
\section{General}
\label{sec:General}
% ----------------------------------------------------------------

This document outlines general information regarding the IF Splitter such as the design, parts, wiring and testing. This information is aimed at detailing the entire process of creating an IF Splitter from design to manufacturing and testing. 

The purpose of the IF Splitter is to divide the incoming signal of one of the tuning (tuning "D" at the ATA) into three separate outputs. First, the signal is divided in two and one half goes directly to an output (3dB attenuation). The second output is divided in two again, leading to two more outputs with 6dB attenuation. This system allows to plug additional equipment (i.e. GNU radio, testing or monitoring devices) without unplugging the main data acquisition channel, making the ATA more polyvalent.

In this document, "IF splitter" designates the whole module while a "power splitter" designate the ZX10-2-12-S+ component that divides a signal in half. One IF splitter 6U module contains 96 power splitter components.
%----------------------------------------------------------------------------------------
%	CAD Design and Drawings
%--------------------------------------------------------------------------------------

\section{CAD Design and Drawings}
\label{sec:CAD}
% ----------------------------------------------------------------
This section includes a description of the CAD design. Figure \ref{fig:CAD_outside} shows the outside of the IF splitter module with the front panel containing the two groups of 6dB outputs. Figure \ref{fig:CAD_inside} shows the IF splitter module open, with the mounts and signal splitter components but no cable. The left CAD drawing shows the back panel with the group of inputs on top and the group of 3dB Outputs below. Both the front and back panel look similar in the number and placement of the SMA connectors. As a visual reference, it can be noted that the two handles are on the front of the IF Splitter. The part list is available in appendix \ref{sec:Part_List}. The Drawings are available in appendix \ref{sec:Drawings}.

\hfill \break

%
\begin{figure}[H]
\centering
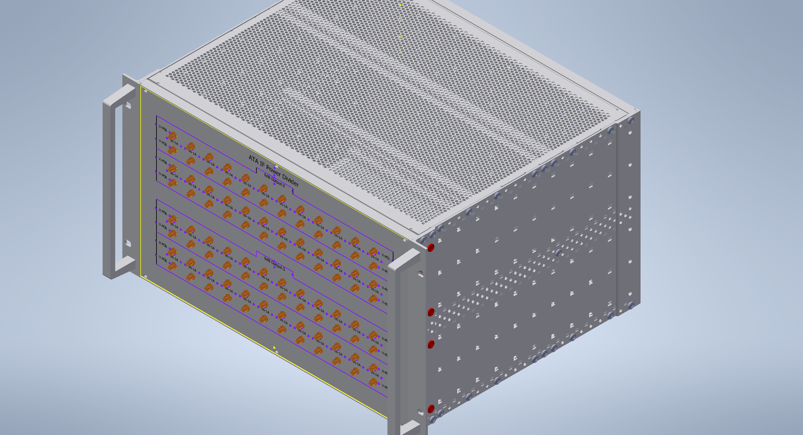
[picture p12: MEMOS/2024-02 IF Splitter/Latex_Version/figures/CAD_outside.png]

\caption{Outside CAD view of the IF splitter.}
\label{fig:CAD_outside}
\end{figure}
%

%
\begin{figure}[H]
\centering
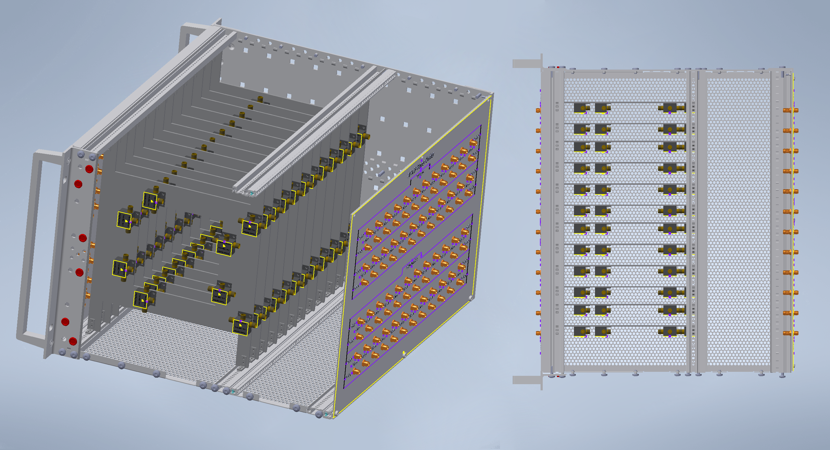
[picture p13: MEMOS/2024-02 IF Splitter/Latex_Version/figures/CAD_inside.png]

\caption{Left shows a three-dimensional CAD view of the inside of the IF splitter. Right shows the same, but from a top view. The cables are not represented on both images for more clarity.}
\label{fig:CAD_inside}
\end{figure}
%

\newpage
\subsection{Design}
\label{sec:Design}
% ----------------------------------------------------------------
The front and back panels each contain two groups of 12$\times$4 SMA connectors. On the back panel, the top group is for the "IF Input" and the bottom for the "3dB Output-1". The front panel contains the two groups of "6dB Output-2" and "6dB Output-3". The front and back panel design are available in appendix \ref{sec:Drawings}. A schematic of the IF Splitter for one input is shown in figure \ref{fig:IF_Splitter_Diagram}. Two inputs are used per antenna for the X and Y polarization signals. Each module contains 48 input connections, which allow to split the signal of 24 antennas. Thus two IF splitter modules are installed for the 42 ATA antennas, leaving 6 input pairs unused for spares.

All the components in the IF splitter are passive so the module doesn't require any power supply.

%
\begin{figure}[H]
\centering
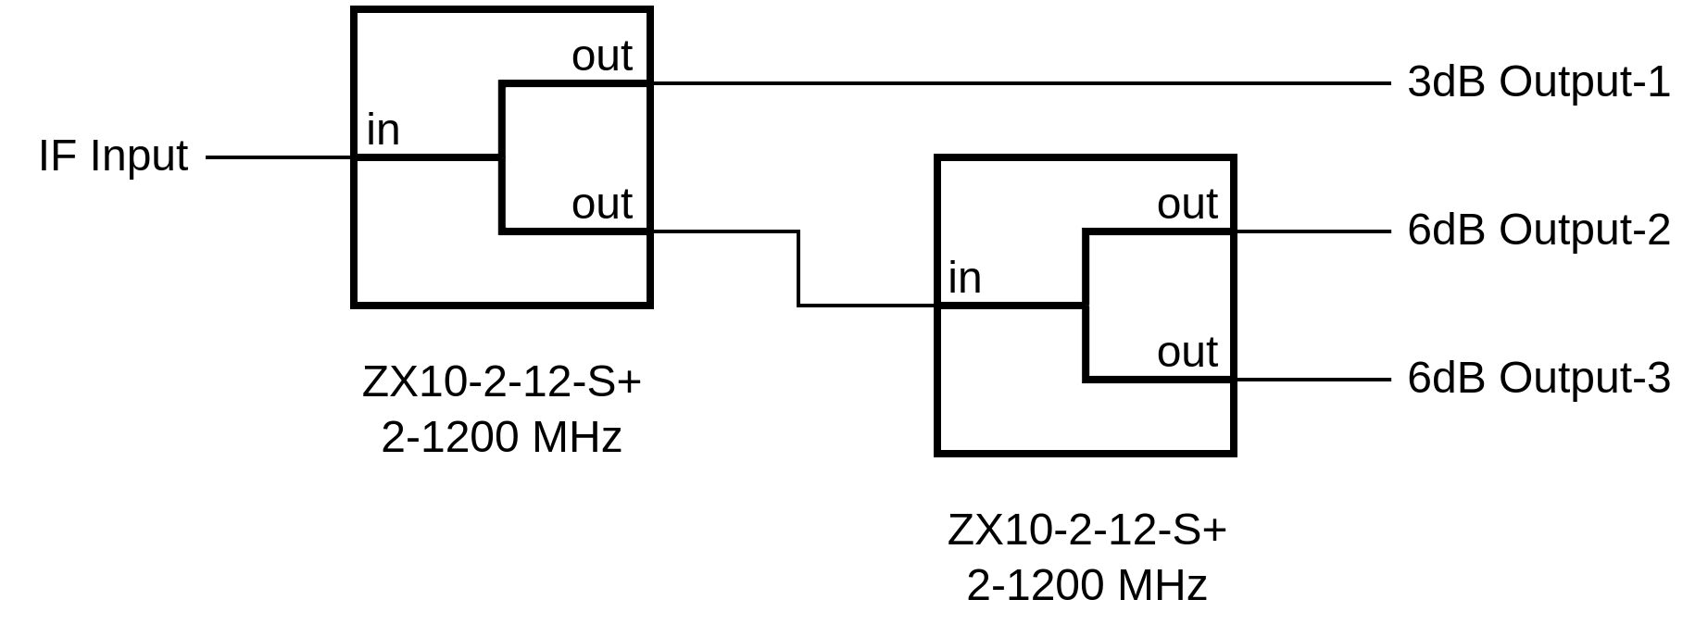
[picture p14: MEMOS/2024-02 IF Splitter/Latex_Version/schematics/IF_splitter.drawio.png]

\caption{Signal splitter diagram for one input, repeated 48 times in the IF Splitter.}
\label{fig:IF_Splitter_Diagram}
\end{figure}
%

%--
\subsection{Wiring}
\label{sec:Wiring}
% ----------------------------------------------------------------
The Mini-Circuits power splitter components are screwed on 12 separate mounts. The wiring schematic of one mount is shown in figure \ref{fig:splitter_full_draw} and a picture of the complete circuit in figure \ref{fig:splitter_wiring}.

%
\begin{figure}[H]
\centering
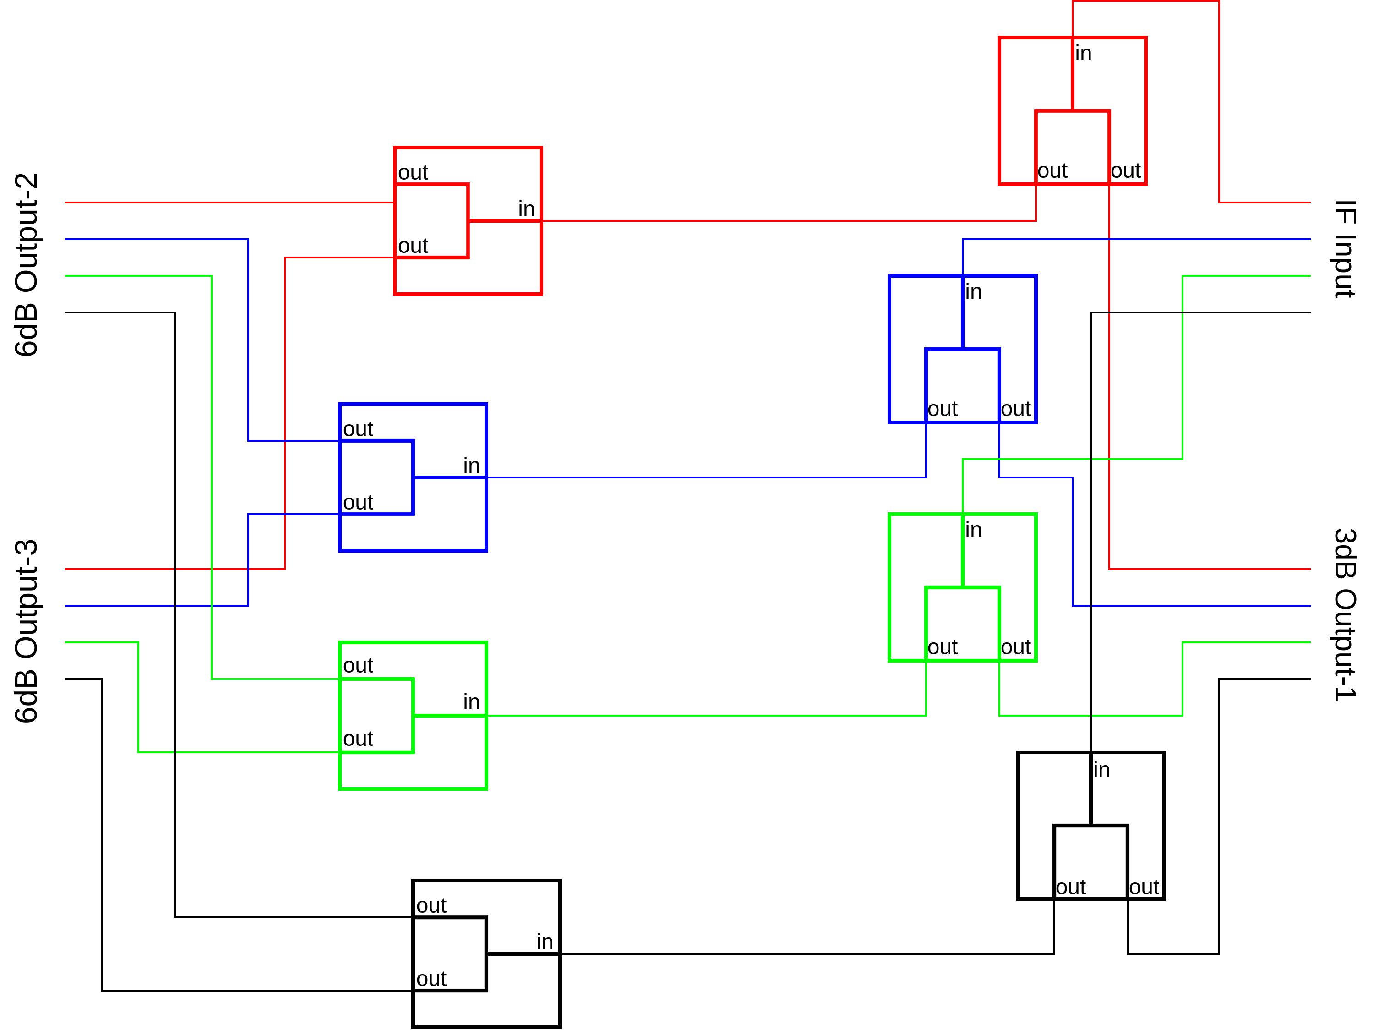
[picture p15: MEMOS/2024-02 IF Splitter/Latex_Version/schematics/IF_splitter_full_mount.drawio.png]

\caption{Wiring diagram for one mount.}
\label{fig:splitter_full_draw}
\end{figure}
%

%
\begin{figure}[H]
\centering

\caption{Picture of one completed mount able to split four input signals.}
\label{fig:splitter_wiring}
\end{figure}
%

\section{Testing}
\label{sec:Testing}

\subsection{Setup}
\label{sec:Testing_Setup}
% ----------------------------------------------------------------
The Vector Network Analyzer (VNA) is used to make a measurement of the scattering matrix. The pre-made "IFSplitter" measurement setup configuration can be selected on the HCRO VNA (Model: Agilient Technologies N5230C) to get the relevant scale and information for the plots. Two 1-meter probe cables "ABC-CA18-SMSM-1.OM" are used. A special wrench that delivers only 0.9$\thinspace$N$\cdot$m or 8$\thinspace$in$\cdot$lbs of torque must be used to tighten all the SMA connectors in place. 

The first step is to calibrate the VNA using the open-short-load calibration kit. In our case, we are not able to calibrate the VNA, hence we use the math function to normalize the $S_{12}$ and $S_{21}$ transmission loss to $0\thinspace$dB over the required frequency range.To do so, both probes are shorted wit a 1.2$\thinspace$cm female-female SMA connector, as shown in figure \ref{fig:VNA_Normalize_Setup}. Then select the scattering matrix plot elements $S_{12}$, $S_{21}$ and select on the VNA: Memory$\rightarrow$Normalize. The result should be $S_{12}=0\thinspace$dB and $S_{21}=0\thinspace$dB for all frequencies on the VNA plots, as shown in figure \ref{fig:VNA_normalized}.

%
\begin{figure}[H]
\centering

\caption{VNA setup for $S_{12}$ and $S_{21}$ normalization.}
\label{fig:VNA_Normalize_Setup}
\end{figure}
%
%
\begin{figure}[H]
\centering
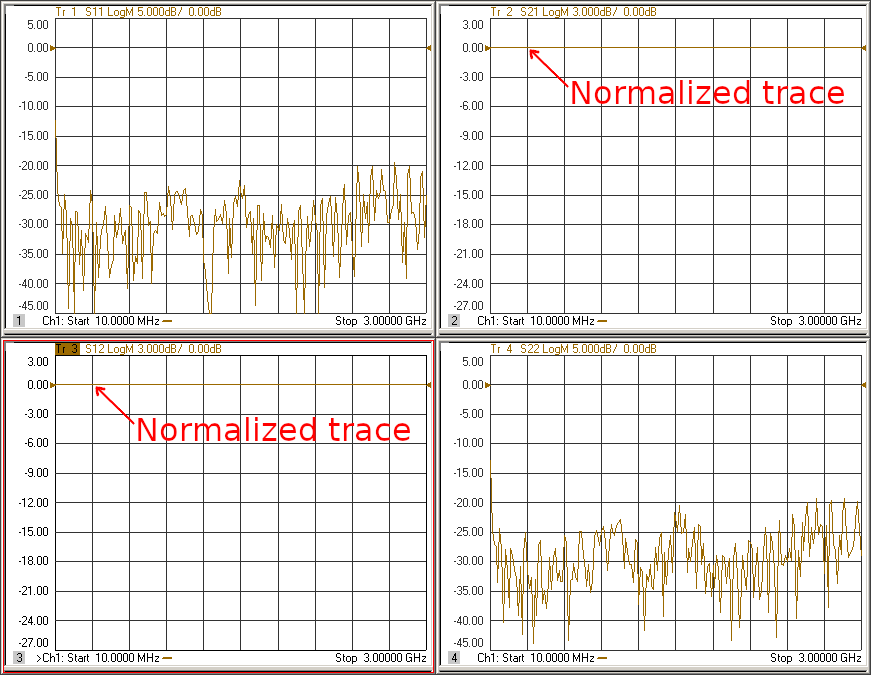
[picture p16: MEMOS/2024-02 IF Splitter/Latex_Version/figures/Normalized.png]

\caption{Scattering matrix after $S_{12}$ and $S_{21}$ normalization.}
\label{fig:VNA_normalized}
\end{figure}
%

\subsection{Method \& Desired Results}
\label{sec:Testing_Method}
% ----------------------------------------------------------------

The VNA port 1 is connected to the "IF Input" while the VNA port 2 is connected in turn to "3dB Output-1", "6dB Output-2" and "3dB Output-3".Two 18$\thinspace$GHz 50$\thinspace\Omega$ terminators are used for the pair of SMA output connectors that are not connected to the VNA. Each measurement is individually recorded as a screenshot of the four S-parameters. These steps have to be reproduced 48 times for all the channels of the IF Splitter module.

An example of the expected measurement of "3dB Output-1" is shown in figure \ref{fig:VNA_3dB-1}. At 10$\thinspace$MHz, $S_{12}$ and $S_{21}$ are slightly below -3dB because of loss. The loss increases significantly after 1.8$\thinspace$GHz, which is above the rated value of 1.2$\thinspace$GHz from the "ZX10-2-12-S+" power splitter. The return loss ($S_{11}$ and $S_{22}$) must be below $-20\thinspace$dB.

The result of for both "6dB Output-2" and "6dB Output-3" must be similar to each-other, the difference being only the output of the second power splitter module. An example is given respectively in figure \ref{fig:VNA_6dB-2} and \ref{fig:VNA_6dB-3}. Here again an increasing loss is observed with the frequency, that accelerate after 1.8$\thinspace$GHz. Also here again the return loss must be below $-20\thinspace$dB.
%
\begin{figure}[]
\centering
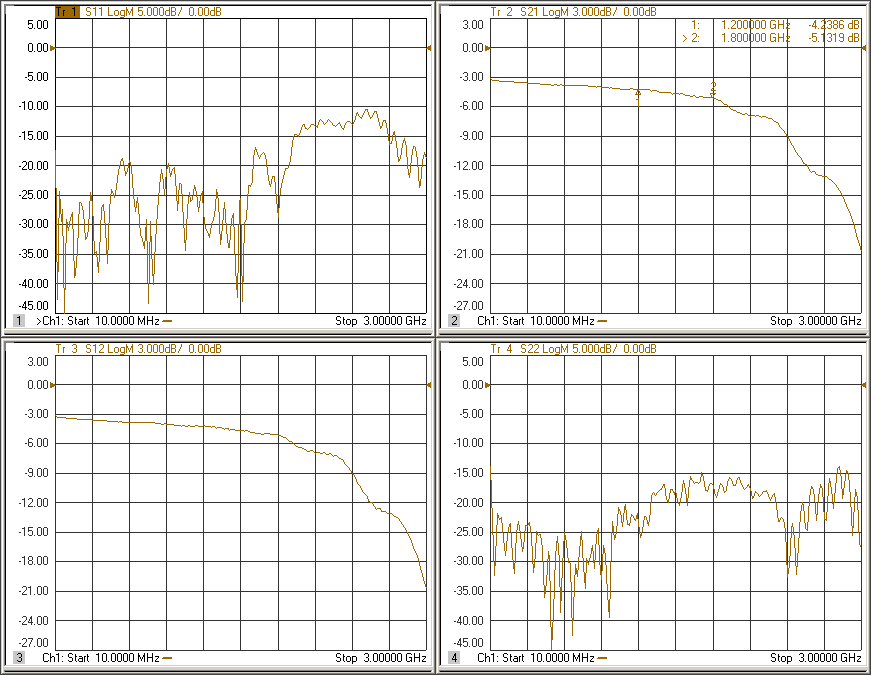
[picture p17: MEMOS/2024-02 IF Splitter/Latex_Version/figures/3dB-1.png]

\caption{Scattering matrix for "3dB Output-1".}
\label{fig:VNA_3dB-1}
\end{figure}
%
%
\begin{figure}[H]
\centering
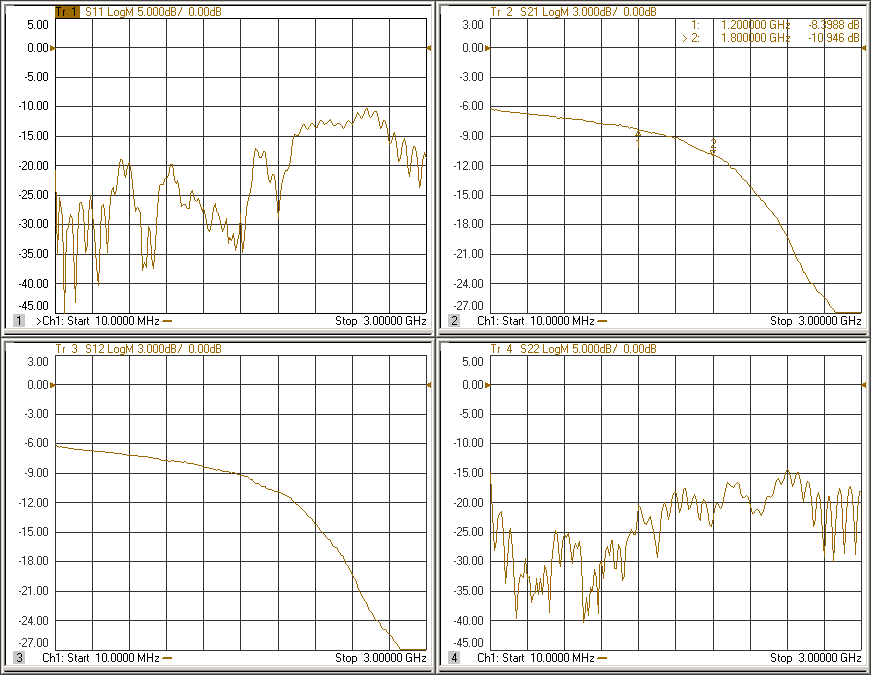
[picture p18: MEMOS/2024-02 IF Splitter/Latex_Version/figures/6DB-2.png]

\caption{Scattering matrix for "6dB Output-2".}
\label{fig:VNA_6dB-2}
\end{figure}
%
%
\begin{figure}[H]
\centering
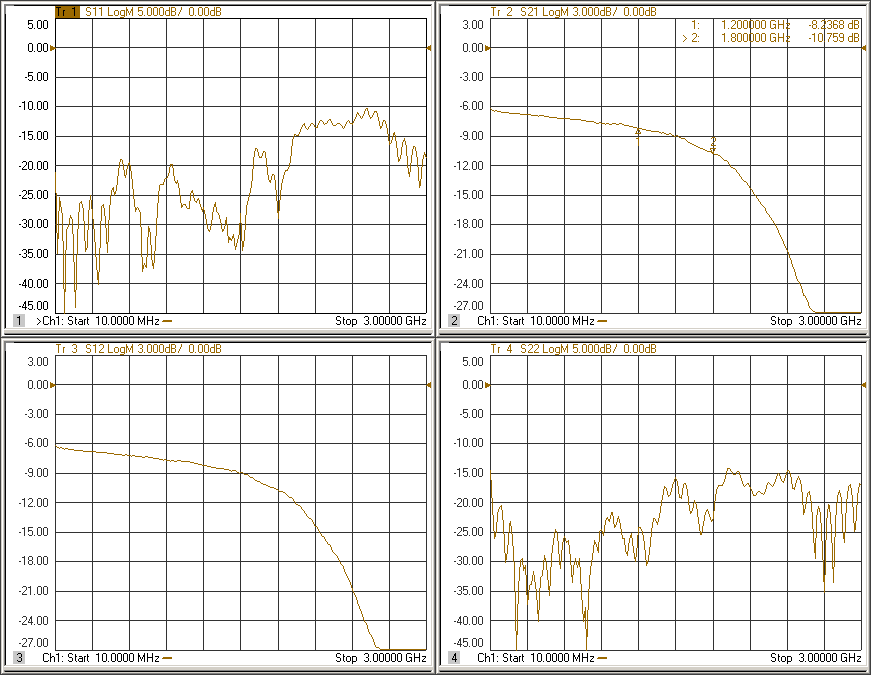
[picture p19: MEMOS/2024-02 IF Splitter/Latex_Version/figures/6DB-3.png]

\caption{Scattering matrix for "6dB Output-3".}
\label{fig:VNA_6dB-3}
\end{figure}
%

\subsection{Module verification}
\label{sec:Testing_Troubleshooting}
% ----------------------------------------------------------------
Each signal path must be measured with the VNA and documented via a measurement result screenshot. If the result doesn't look like the example figures \ref{fig:VNA_3dB-1} to \ref{fig:VNA_6dB-3}, look at the different output measurement for a same input to try to locate the problem with the schematic in figure \ref{fig:IF_Splitter_Diagram}. If there is no transmission, verify that the circuit corresponds to the schematic in figure \ref{fig:splitter_full_draw}. 

If the transmission signal curves of $S_{12}$ and $S_{21}$ aren't smooth (figures \ref{fig:VNA_3dB-1} to \ref{fig:VNA_6dB-3} show how they should look), there must be a bad connection along the signal path. First verify that the probes and terminators are attached correctly on the front panel with the right amount of torque. Then have a visual inspection of the mount and connection to verify that no component is damaged or not mounted properly. If everything looks good, it can either be a bad cable connection or a bad power splitter. If all the cables are connected and torqued properly, verify the power splitter modules themselves by plugging the VNA to their output directly. The unused third connector must be terminated. Finally, if the problem is still there, test the cables themselves using the VNA.
\newpage
 
%----------------------------------------------------------------------------------------
%	Appendix: Attemplifier Module Enclosure Drawings
%----------------------------------------------------------------------------------------

\appendix
% ----------------------------------------------------------------

% To include pages from other PDFs
% \includepdf[pages=-, landscape=true]{Documentation/PDFs/24567174_05(copy).pdf}

%----------------------------------------------------------------------------------------
%	Appendix: IF splitter Component List
%----------------------------------------------------------------------------------------
\begin{landscape}
\section{Component List of the IF Splitter}\label{sec:Part_List}

% ----------------------------------------------------------------

\begin{table}[H]
\centering
\resizebox{1.5\textwidth}{!}{%
\begin{tabular}{@{}lllllll@{}}
\toprule
Qty & Unit & Description & Manufacturer & PN Manufacturer & Distributor & PN Distributor\\
\midrule
1 & Each & 6U EuropacPRO kit, heavy design, shielded, without front handles & Schroff & 24563-474 & Distrelec & 110-28-346 \\
1 & Each & Front Panel & Front Panel Express, LLC & ATA-IFD-AP-24567274\_100F.fpd &&\\
1 & Each & Rear panel & Front Panel Express, LLC & ATA-IFD-AP-24567274\_100R.fpd &&\\
12 & Each & Mounting Panel & Front Panel Express, LLC & ATA-IFD-AP-24567274\_200.fpd &&\\
48 & Each & Mounting Bracket & Front Panel Express, LLC & ATA-IFD-AP-24567274\_201.fpd &&\\
96 & Each & 2 Ways Power Splitter, 2 - 1200 MHz, 50$\Omega$ & MiniCircuit & ZX10-2-12-S+ &&\\
%
4 & Pack & Machine Screw, M2.5, 5mm & TR FASTENINGS & 173-202579H & Newark & 25M0782\\
% 1 pach is 100 screw and we need 336:
% 12 * 12 = 144 for L-brackets
% 16 * 12 = 192 to attach power splitter modules on mount
%

48 & Each & 5 Inch SMA coaxial cable & Atlantic Microwave & ASF1-005-520003-S4S4 &&\\
96 & Each & 6 Inch SMA Male to SMA Female Bulkhead cable & Pasternack & PE39433-6 &&\\
96 & Each & 12 Inch SMA Male to SMA Female Bulkhead cable & Pasternack & PE39433-12 &&\\
\bottomrule            
\end{tabular}}
\label{tab:IF_components}
\end{table}

%----------------------------------------------------------------------------------------
%	Appendix: Control Board Schematics
%----------------------------------------------------------------------------------------

\section{Drawings}
\label{sec:Drawings}
Below are the drawings of the back panel, Power Splitter Mount and L-shape attachment brackets.
\includepdf[pages=1-2, landscape=true]{PDFs/24567474_100.pdf}
\includepdf[pages=-, landscape=true]{PDFs/24567474_200.pdf}
\includepdf[pages=-, landscape=true]{PDFs/24567474_201.pdf}
% ----------------------------------------------------------------

\end{landscape}

%
%\begin{figure}[H]
%\centering
%\includegraphics[width=1\linewidth]{<path>/picture.png}
%\caption{Caption}
%\label{fig:LABEL}
%\end{figure}
%

\end{document}

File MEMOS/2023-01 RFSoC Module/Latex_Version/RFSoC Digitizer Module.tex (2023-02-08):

\documentclass[12pt,a4paper,oneside]{article}
\usepackage[margin=1.2in]{geometry}
\usepackage{appendix}
\usepackage[dvips]{graphicx}
\usepackage{epsfig}
\usepackage{amsmath}
\usepackage{amssymb}
\usepackage{psfrag}
\usepackage[square, comma,sort,numbers]{natbib}
\usepackage{fancyhdr}
\usepackage[nottoc]{tocbibind}
\usepackage{color}
\usepackage{fixltx2e}
\usepackage{pdfpages}
\usepackage{pdflscape}
\usepackage{booktabs}
\usepackage{graphicx}
\usepackage{float}
\usepackage{afterpage}
\usepackage{subcaption}
\usepackage{lscape}
\usepackage{rotating}
\usepackage{enumitem}
\usepackage{array,tabularx}
\usepackage{fancyref}
\usepackage{gensymb}
\usepackage[dvipsnames]{xcolor}
\usepackage[colorlinks=true,allcolors=blue]{hyperref}%

\newcommand{\quotes}[1]{``#1''}

\newenvironment{conditions*}
  {\par\vspace{\abovedisplayskip}\noindent
   \tabularx{\columnwidth}{>{$}l<{$} @{\ : } >{\raggedright\arraybackslash}X}}
  {\endtabularx\par\vspace{\belowdisplayskip}}

\pagestyle{fancy}
\title{\Huge The Hat Creek Radio Observatory\\
\vspace{0.5cm}
The RFSoC Digitizer Module\\
\vspace{0.5cm}
\normalsize \emph{}
\vspace{3.5cm}
\begin{center}

\end{center}
}
\author{ 
\vspace{1cm}
\Large
\textbf{ Alexander Pollak \& Sarah Schoultz} \\
SETI Institute \\ 
339 Bernardo Ave, Suite 200 \\
Mountain View, CA 94043 \\ 
Alexander.Pollak.87@gmail.com\\
}
\date{\today}

\begin{document}
\clearpage\maketitle
\thispagestyle{empty}

%\newpage
%\thispagestyle{empty}
%\section*{Abstract}
%\noindent 
%

%
%\vspace{3cm}
%\begin{flushright}
%Alexander Pollak \\ \emph{September, 2015}
%\end{flushright}

%\newpage
%\thispagestyle{empty}
%\tableofcontents
\newpage

%----------------------------------------------------------------------------------------
%	General
%----------------------------------------------------------------------------------------
%\pagestyle{plain}
\section{General}
\label{sec:1}
% ----------------------------------------------------------------
This document outlines general information regarding the RFSoC Digitizer Module such as the design, parts, wiring, and cabling. This information is aimed at detailing the entire process of creating an RFSoC Digitizer Module.

The purpose of an RFsoC Digitizer Module is to digitize the analog signals detected by the ATA's antennas. Once digitized, the signals can be saved and analyzed. This digitizer is a replacement for the ATA's previous digitizers called SNAPs and IBOBs. With sixteen 14-bit ADCs, two 100 G outputs, a larger FPGA, and more up to date technology, the RFSoC Digitizer Module is vast improvement upon the previous hardware. 

%----------------------------------------------------------------------------------------
%	CAD Design and Drawings
%--------------------------------------------------------------------------------------

\section{CAD Design and Drawings}
\label{sec:2}
% ----------------------------------------------------------------
This section includes a description of the RFSoC Digitizer Module's CAD design. An image of the CAD model is shown in Figure \ref{fig:CAD-Iso} and \ref{fig:CAD-top}. One can see the internal arrangement of the HTG-ZRF16 board (middle rear), power supply (front right), and directional fans (left rear and front right). The lid of the enclosure, not shown in this Figure, is perforated to further increase cooling. The panel facing the viewer in Figure \ref{fig:CAD-Iso} is considered the front panel. This is important to note for future sections. The majority of the RFSoC Digitizer Module's enclosure is off the shelf (PN: 24563-174) except for a few parts: the front panel, the back panel, the base plate, and the cable clamp. These custom parts were made by Front Panel Express, and the drawings can be found in Appendix A. 

%
\begin{figure}[H]
\centering
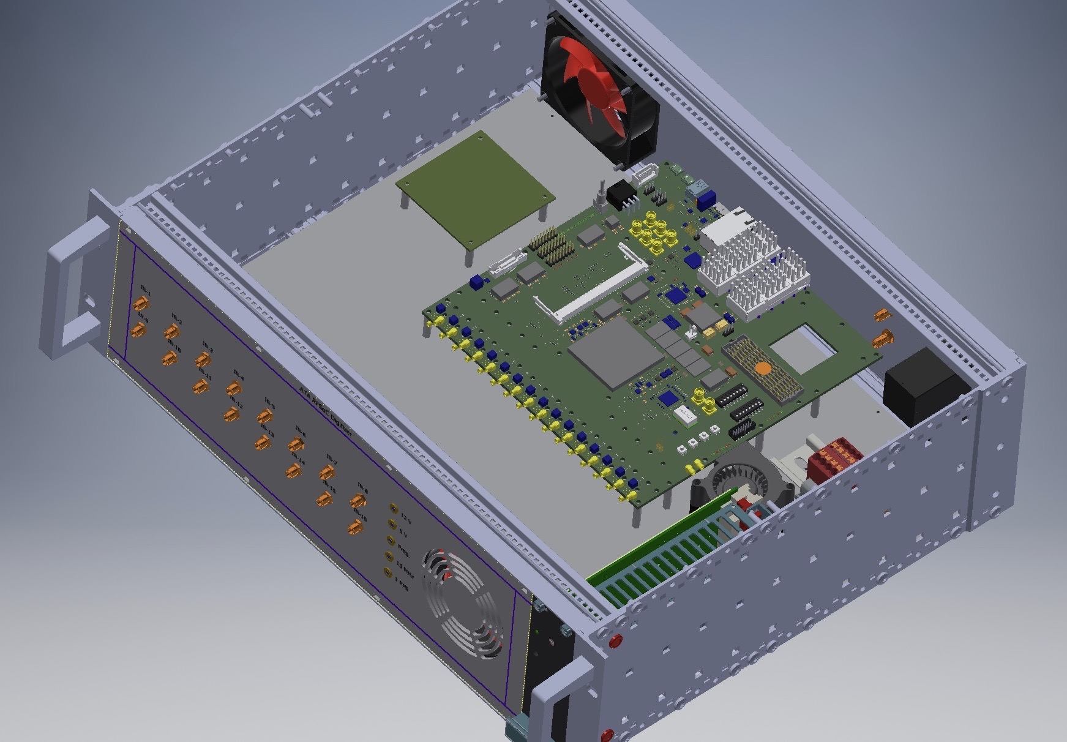
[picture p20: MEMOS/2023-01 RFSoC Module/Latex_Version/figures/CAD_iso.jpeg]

\caption{ISO view of the RFSoC CAD}
\label{fig:CAD-Iso}
\end{figure}
%

%
\begin{figure}[H]
\centering
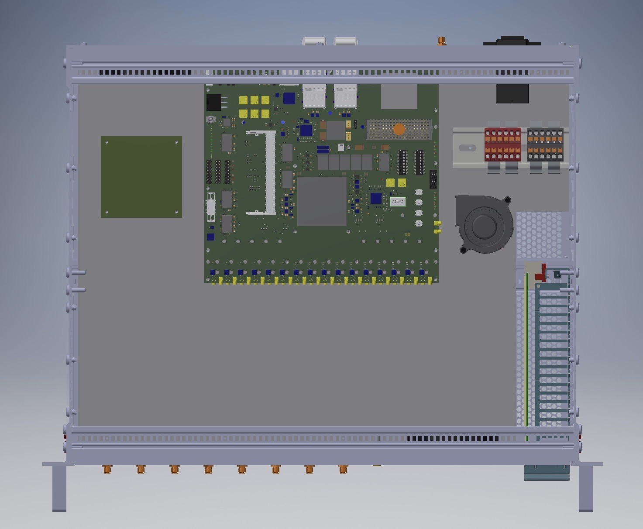
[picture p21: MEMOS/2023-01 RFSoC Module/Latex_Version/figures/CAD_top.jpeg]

\caption{Top View of the RFSoC CAD}
\label{fig:CAD-top}
\end{figure}
%

For a part list of the RFSoC Digitizer Module, except for the HTG-ZRF16 board and the  Interface Board,  see Appendix B. 

%----------------------------------------------------------------------------------------
%	HTG-ZRF16 Board
%---------------------------------------------------------------------------------------

\section{HTG-ZRF16 Board}
\label{sec:3}
% ----------------------------------------------------------------

The HTG-ZRF16 board, seen in Figure \ref{fig:HTG-ZRF16_Board}, is a product of HiTech Global. It is populated with a Xilinx ZYNQ UltraScale+ RFSoC ZU49DR FPGA. There are two on-board 100Gbps QSFP28 connectors allowing high-speed data processing via an optical interface. The board also has sixteen 14-bit ADCs with a sampling rate of 2.5 GSPS. 

%
\begin{figure}[H]
\centering
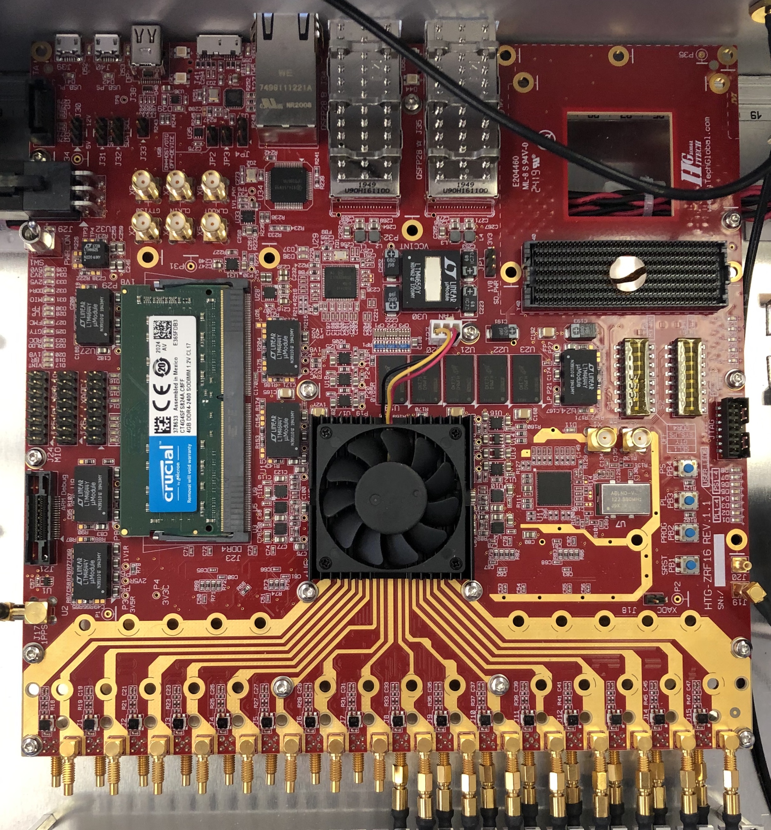
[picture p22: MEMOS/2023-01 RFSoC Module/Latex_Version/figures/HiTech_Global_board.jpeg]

\caption{The HTG-ZRF16 Board Produced by HiTech Global}
\label{fig:HTG-ZRF16_Board}
\end{figure}
%

At the ATA, the RFSoC Digitizer Modules are operated at a sample rate of 2.048 GSPS. This is because the IF bandwidth is 700 MHz and centered at 512 MHz thus giving the system a 162 MHz leeway to prevent aliasing. Note that due to a known flaw, the HTG-ZRF16 boards purchased for the ATA were retrofitted by HiTech Global (Figure \ref{fig:Digitizer_retrofit}). Specifically, pin 44 (OSCin) of the LMK PLL chip was \emph{not} AC-coupled to ground as it should have been and was instead connected directly to ground. Hence, HiTech Global installed a capacitor in between pin 44 of the LMK PLL chip and ground as a retrofit for this issue. 

%
\begin{figure}[H]
\centering
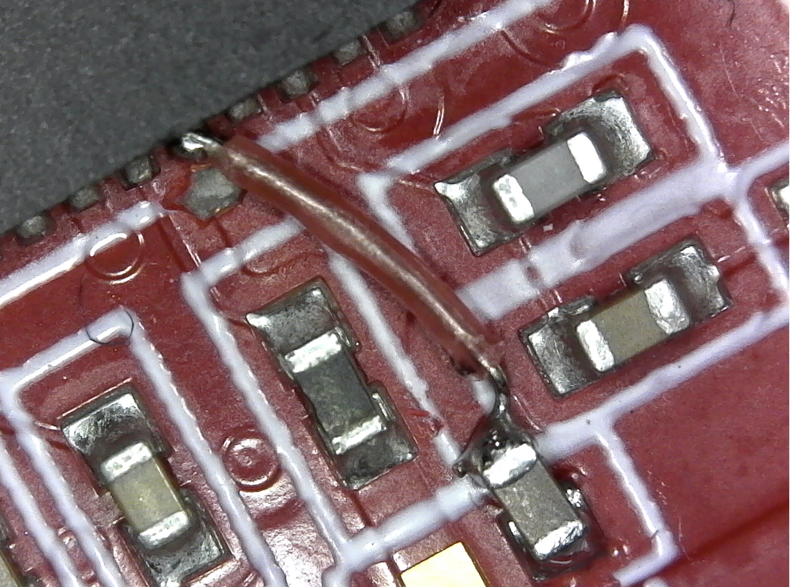
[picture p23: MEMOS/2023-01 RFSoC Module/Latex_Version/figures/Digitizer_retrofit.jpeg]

\caption{The HTG-ZRF16 Board with Capacitor Retrofit on Pin 44 of the of the LMK PLL Chip}
\label{fig:Digitizer_retrofit}
\end{figure}
%

\subsection{Heat Sink Fan}
\label{sec:3.1}

While in use, the FPGA can reach high temperatures. Hence, the HTG-ZRF16 board comes with a heat sink fan mounted onto the FPGA (Figure \ref{fig:Old_heatsink_fan}). However, during initial use of the first RFSoC Digitizer Module, the temperature of the FPGA reached $90-95\degree C$ which is uncomfortably close to the FPGA's maximum temperature of $100\degree C$. It was, therefore, determined that the original heat sink fan was insufficient at keeping  the FPGA's temperature within acceptable levels and so was removed (Figure \ref{fig:FPGA}).

%
\begin{figure}[H]
\centering
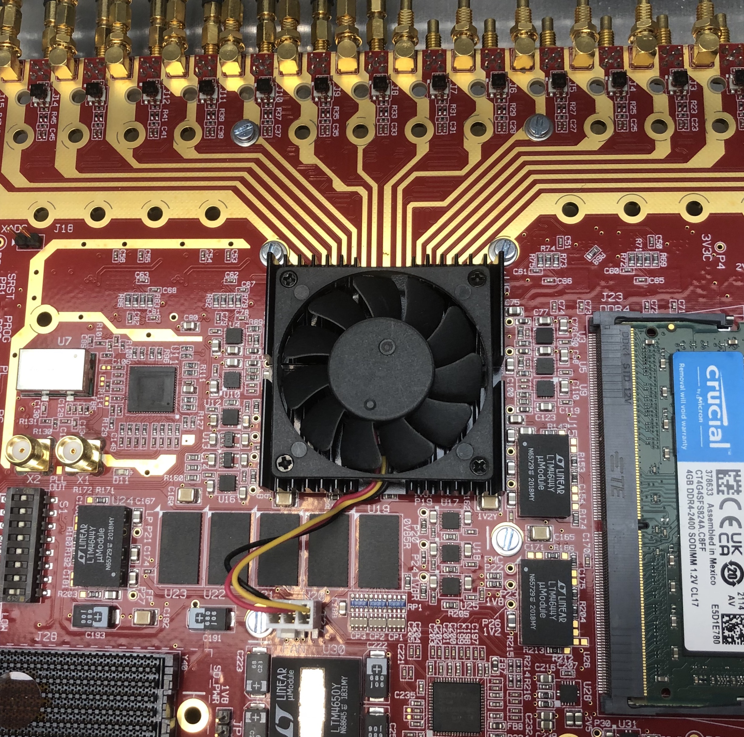
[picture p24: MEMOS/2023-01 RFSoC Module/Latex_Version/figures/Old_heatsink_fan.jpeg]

\caption{HTG-ZRF16 Board with the HiTech Global Heat Sink Fan}
\label{fig:Old_heatsink_fan}
\end{figure}
%

%
\begin{figure}[H]
\centering

\caption{The HTG-ZRF16 Board's FPGA with the HiTech Global Heat Sink Fan Removed}
\label{fig:FPGA}
\end{figure}
%

In place of the HiTech Global heat sink fan, a new heat sink (PN: ATS-55450W-C1-R0) and fan (PN: AFB04512HA) were installed (Figure \ref{fig:New_heat_sink_fan}). This pairing was able to reduce the temperature to $60-65\degree C$ which was deemed acceptable. 

%
\begin{figure}[H]
\centering

\caption{The HTG-ZRF16 Board with the New Heat Sink and Fan Installed}
\label{fig:New_heat_sink_fan}
\end{figure}
%

%----------------------------------------------------------------------------------------
%	Interface Board
%--------------------------------------------------------------------------------------

\section{Interface Board}
\label{sec:4}
% ----------------------------------------------------------------

The Interface Board is designed as junction between to the HTG-ZRF16 board and the front panel LEDs which indicate the functionality status of the HTG-ZRF16 board. Assembled in house, Figure \ref{fig:Interface_Board} shows how a completed Interface Board should look. A list of all its required parts appears in Appendix C. 

%
\begin{figure}[H]
\centering

\caption{Completed Interface Board}
\label{fig:Interface_Board}
\end{figure}
%

\subsection{Design}
\label{sec:4.1}
% ----------------------------------------------------------------

The Interface Board electrically isolates any signals from the HTG-ZRF16 board via optocouplers (OK1 and OK2) to avoid any noise contamination. The board is designed to accept 9-25V DC as an input and includes several yellow LEDs (HTG-5V, HTG-12V, HTG 5V, HTG 12V, and Ctl. 5V) that indicate the supply voltage of the HTG-ZRF16 board and Interface Board. Additionally, there are green LEDs (GPIO-1 through GPIO-6) for the HTG-ZRF16 board's GPIOs. Currently, only GPIO 1-3 are used and are set to indicate the HTG-ZRF16 board programming status, the 10 MHz signal, and the 1 PPS signal. Both the green and yellow LEDs are duplicated on the front panel of the module and are connected to the Interface Board via pin-headers. All of these functionalities are reflected in the schematic, Appendix D, and layout, Figure \ref{fig:Interface_Layout}, of the Interface Board. The Interface Board voltage range is 9-25V.

%
\begin{figure}[H]
\centering

\caption{Interface Board Layout}
\label{fig:Interface_Layout}
\end{figure}
%

%----------------------------------------------------------------------------------------
%	Power Supply
%----------------------------------------------------------------------------------------
\section{Power Supply}
\label{sec:5}
% ----------------------------------------------------------------

The module's HTG-ZRF16 board, cooling fans, and the Interface Board are powered with a Schroff Max 180 (PN: 13100-151). The unit is mounted directly to the front panel of the enclosure. The operating temperature range of the power supply is from $-25^{\circ}$C through $85^{\circ}$C, and the technical specifications are shown in Table \ref{tab:psu_spec}. The power entry module (PN: 4304.4005), mounted in the back panel, combines an IEC inlet and a mains filter with a dual-fuse holder. The AC supply fuse current rating for this unit is selected to be 2\,A (PN: 0239002.HXP). 

\begin{table}[H]
\centering
\caption{Power Supply Specification}
\label{tab:psu_spec}
\begin{tabular}{@{}ccccc@{}}
\toprule
\multicolumn{1}{l}{Description} & \multicolumn{1}{l}{Output Voltage} & \multicolumn{1}{l}{Output Current} & \multicolumn{1}{l}{Power W} & \multicolumn{1}{l}{Input Voltage} \\ \midrule
MAX180-112                         & 12\,VDC                               & 13A                               & 156W                         & $100 \sim 240\,\rm{VAC}$                              \\ \bottomrule
\end{tabular}
\end{table}

%----------------------------------------------------------------------------------------
%	Enclosure Wiring
%--------------------------------------------------------------------------------------

\section{Enclosure Wiring}
\label{sec:6}
% ----------------------------------------------------------------

This section outlines the internal connections of the RFSoC Digitizer Module. It is broken up into how parts connect to the front panel, the Interface Board, the HTG-ZRF16 board, the power supply, and the power entry module. Note that there are parts required for wiring the module that do not appear on part lists. This is because they are considered on-hand supplies. These parts include shrink tube, solder, hook up wire, and common terminals.

\subsection{Front \& Back Panel}      
\label{sec:6.1}
% ----------------------------------------------------------------

This section includes the locations of where cables enter the module and connect to the HTG-ZRF16 board within. 

\begin{table}[H]
\caption{Cable Connections for Front Panel}
\centering
\begin{tabular}{@{}ccc@{}}
\toprule
Panel Label & Board Connector Number & Type of Board Connector\\ 
\midrule
IN-1 & J9 & SSMC\\
IN-2 & J10 & SSMC\\
IN-3 & J11 & SSMC\\
IN-4 & J12 & SSMC\\
IN-5 & J13 & SSMC\\
IN-6 & J14 & SSMC\\
IN-7 & J15 & SSMC\\
IN-8 & J16 & SSMC\\
IN-9 & J51 & SSMC\\
IN-10 & J52 & SSMC\\
IN-11 & J53 & SSMC\\
IN-12 & J54 & SSMC\\
IN-13 & J55 & SSMC\\
IN-14 & J56 & SSMC\\
IN-15 & J57 & SSMC\\
IN-16 & J58 & SSMC\\

\bottomrule            
\end{tabular}
\label{table:front_panel}
\end{table}

\begin{table}[H]
\caption{Cable Connections for Back Panel}
\centering
\begin{tabular}{@{}ccc@{}}
\toprule
 Panel Label & Board Connector Number & Type of Board Connector\\ 
\midrule
1 PPS & J17 & MCX\\
10 MHz & J19 & SSMC\\
100 GbE P0 & J35 & QSFP28\\
100 GbE P1 & J34 & QSFP28\\
1 GbE & J37 & RJ45\\

\bottomrule            
\end{tabular}
\label{table:back_panel}
\end{table}

\subsection{Interface Board}
\label{sec:6.2}

The Interface Board is connected to the power supply (PN: 13100-151 ), the HTG-ZRF16 board, and the LEDs (PN: Q6F7BXXB02E).

For the power supply connection, a twisted pair of red and black 18 awg wire was made. Then two E7508 gray ferrules were crimped onto one end and inserted into a 2 Way Cable Mount Screw Terminal (PN: 1803578). This then plugs into the straight PCB terminal block header (PN: 1803426) labeled X1 on the Interface Board.  

The HTG-ZRF16 board is connected to the Interface Board via a a 16 to 16 GPIO Ribbon Cable (PN:IDSD-08-D-06.00) and a twisted triplet of yellow, black, and orange 24 awg wire. The GPIO Ribbon Cable provides the status of GPIO's 1-3 to the green LEDs while the twisted triplet provides the status of power to the HTG-ZRF16 board (HTG 5V and 12V) to the yellow LEDs. The GPIO Ribbon Cable plugs into HTG-J25-GPIO on the Interface Board and J25 on the HTG-ZRF16 board. The twisted triplet was crimped with M20 Crimp Terminals (PN:M20-1180042) which were then inserted into a 3 Pin SIL Housing (PN: M20-1060300). The twisted triplet plugs into HTG-J30-Supply on the Interface Board and J30 on the HTG-ZRF16 board. See Figure \ref{fig:power_indicator_cable} for how the triple if orientated on each board. 

\begin{figure}[H]
\centering

\caption{HTG-ZRF16 and Interface Board's Cable Orientations}
\label{fig:power_indicator_cable}
\end{figure}

The five LEDs' wires are extended with red and black 28 awg as to reach the Interface Board. They are then crimped with M20 Crimp Terminals which are inserted into a 2 Pin SIL Housing (PN: M20-1060200). The Interface Board has eight two pin Straight PCB Headers (PN: 42375-2486), five of which the LEDs plug into. Table \ref{LED_to_board} shows which LEDs plug into which headers on the board. 

\begin{table}[H]
\caption{LED Internal Cable Connections}
\centering
\label{LED_to_board}
\begin{tabular}{@{}cc@{}}
\toprule
 LED Panel Label & Board Connector Label\\ 
\midrule
12V & HTG-12V\\
5V & HTG-5V\\
Prog. & GPIO-1\\
10 MHz & GPIO-2\\
1 PPS & GPIO-3\\

\bottomrule            
\end{tabular}
\label{table:LED_to_board}
\end{table}

% ----------------------------------------------------------------

\subsection{HTG-ZRF16 Board}
\label{sec:6.3}

The HTG-ZRF16 board connects to the power supply (PN: 13100-151), Interface Board, the heat sink fan (PN: AFB04512HA), front panel, and back panel.

The power supply is connected to the HTG-ZRF16 board via six wires, three red for 12V and three black for ground. The six wires are 18 awg and are twisted into pairs. Each wire is crimped with a Minifit plus terminal (PN: 45750-1112) and then all six are plugged into a Molex Minifit Jr. 6 Socket Receptacle (PN: 45559-0002) as shown in Figure \ref{fig:board-power}. Before installation, check the polarity. Figure \ref{fig:power_indicator_cable} shows how the cable looks once completed and how it should be orientated. 

\begin{figure}[H]
\centering

\caption{The Molex board power adapter}
\label{fig:board-power}
\end{figure}

The Interface Board connections to the HTG-ZRF16 board are outlined in the Interface Board section above. 

As noted in the Section \ref{sec:4}, the HTG-ZRF16 board has a heat sink fan due to high temperature while in use. This heat sink fan is connected directly to the board for power via J27. Though, prior to being plugged in, the fan's wires are twisted together, crimped with M20 Crimp Terminals (PN:M20-1180042), and inserted into a 2 Pin SIL Housing (PN: M20-1060200). 

The front and back panel connections to the HTG-ZRF16 board are outlined in Table \ref{table:front_panel} and \ref{table:back_panel}. The 100 GbE P0, 100 GbE p1, and 1 GbE connections from the back panel plug directly from the back panel into the HTG-ZRF16 board. The rest of the back panel connections and all the front panel connections are done via SMA Female Bulkhead to SSMC Plug Cables (PN: PE3C4448-18),

% ----------------------------------------------------------------

\subsection{The Fans}
\label{sec: the 6.4}

There are a total of ten fans inside the RFSoC Digitizer Module. The first of these is the heat sink fan (PN: AFB04512HA) which was already discussed in the previous section. The rest of the fans are connected to the power supply. There is the front panel fan (PN: PF80251V1-1000U-A99), the back panel fan (PN: PF80251V1-1000U-A99), the blower fan (PN: GB1205PKV1-8AY.GN), and six base plate fans (PN: 412FM). The front panel and back panel fans wires are extended with red and black 20 awg in order to reach the power supply. The blower fan's wires are long enough as is, and the six base plate fans' wires are soldered together and extended with and red and black 20 awg wires. 

Regarding how the fans should be mounted, the front panel fan should blow air into the enclosure while the back panel to sucks air out of the enclosure. The six base plate fans should be mounted such that they blow air into the enclosure. The front panel, back panel, and blower fan can all be seen in Figures \ref{fig:CAD-Iso} and \ref{fig:CAD-top}. However, the six base plate fans are not visible, nor can they be seen in the completed enclosure (Figures \ref{fig:Enclosure_above} through \ref{fig:Enclosure_in_Rack}). Figure \ref{fig:six_fan_front} and \ref{fig:six_fan_back}, instead, shows an incomplete RFSoC Digitizer Module with the six base plate fans visible.

\begin{figure}[H]
\centering

\caption{Front view of an incomplete RFSoC Digitizer Module}
\label{fig:six_fan_front}
\end{figure}

\begin{figure}[H]
\centering

\caption{Back and upside down view of an incomplete RFSoC Digitizer Module}
\label{fig:six_fan_back}
\end{figure}

% ----------------------------------------------------------------

\subsection{Power Supply}
\label{sec: the 6.5}

The power supply (PN: 13100-151) is connected to the Interface Board, the HTG-ZRF16 board, the fans, and the power entry module (PN: 4304.4005). 

Due to the large number of components requiring power, the power supply uses a set of power distribution terminals (PN: 3273158 and 3273168) shown in Figure \ref{fig:Power_Distribution Terminals}. Please see Figure \ref{fig:RFSoC_Power_Schematic_1} for a schematic that shows how the power supply is connected to the power distribution terminals. The red and black wires used are 14 awg and are both crimped with female quick disconnect terminals (PN: FDFD1-250) on the ends plugging into the power supply. The ends plugging into the power distribution terminal are just stripped. There is also a green ground wire that connects the black power distribution module to the base plate. This wire is stripped on the power distribution terminal end and crimped with a 6s eye terminal on the other. The eye terminal is screwed down to the base plate.

\begin{figure}[H]
\centering

\caption{The Power Distribution Terminals Installed in the RFSoC Digitizer Module}
\label{fig:Power_Distribution Terminals}
\end{figure}

A schematic of how the power distribution terminals are connected to the Interface Board, the HTG-ZRF16 board, and the fans is shown in Figure \ref{fig:RFSoC_Power_Schematic_2}. See the above sections for wires gauges, terminals, and housings used for all these connections. 

How the power supply is connected to the power entry module is shown in Figure \ref{fig:RFSoC_Power_Schematic_1}. The black and white wires are crimped on both ends with female quick disconnect terminals. The green ground wire for the power supply has female quick disconnect terminals on both ends as well, and rather than being connected directly to the base plate, it instead plugs into the female piggyback disconnect terminal (PN:
PBDD2-250) of the power entry module's ground wire. 

\begin{figure}[H]
\centering

\caption{RFSoC Digitizer Module Power Schematic Part 1. This half of the power schematic shows the connections between the power entry module, the power supply, and the two power distribution terminals. The colors of the connections represent the color of wire used. All the wires connecting the to the power entry module and base plate are 16 awg. The rest of the wire gauges are specified  in the power supply subsections.}
\label{fig:RFSoC_Power_Schematic_1}
\end{figure}

\begin{figure}[H]
\centering

\caption{RFSoC Digitizer Module Power Schematic Part 2. This half of the power schematic shows the connections of the two power distribution terminals, the fans, the HTG-ZRF16 board, and the Interface Board. The colors of the connections represent the color of wire used. The wire gauges are specified  in the power supply subsections.}
\label{fig:RFSoC_Power_Schematic_2}
\end{figure}
% ----------------------------------------------------------------

\subsection{The Power Entry Module}
\label{sec:6.6}
% ----------------------------------------------------------------

The power entry module (PN: 4304.4005) is connected to the power supply (PN: 13100-151) and the base plate. Refer to Figure \ref{fig:RFSoC_Power_Schematic_1} for the wiring schematic of the power entry module.

Th power supply connection to the power entry module was already described in the previous section. The base plate is connected to the power entry module via a green 12 awg wire crimped with a 6s eye terminal on one end and a female piggyback disconnect terminal (PN:
PBDD2-250) on the other. The 6s eye terminal is screwed into the base plate while the female piggyback disconnect terminal plugs into the power entry module. Note that this is the female piggyback disconnect terminal that has the the green ground wire from the power supply plugging into it. 

%----------------------------------------------------------------------------------------
%	Completed Module
%----------------------------------------------------------------------------------------
\section{Completed Module}
\label{sec:7}
% ----------------------------------------------------------------

Upon completion, an assembled RFSoC Digitizer Module is shown in the Figures \ref{fig:Enclosure_above}, \ref{fig:Front_completed}, \ref{fig:Back_complete}, and \ref{fig:Enclosure_in_Rack}. The biggest difference between the finished enclosure and the CAD design is the wiring, screws, lids, and cable clamp (front middle between the front panel and RFSoC board in Figure \ref{fig:Enclosure_above}) which were all left out in the CAD (Figures \ref{fig:CAD-Iso} and \ref{fig:CAD-top}). Note that the new heat sink and fan had not yet been installed on the HTG-ZRF16 board in Figure \ref{fig:Enclosure_above}. Furthermore, Figures  \ref{fig:Front_completed} and \ref{fig:Back_complete} is missing the HTG-ZRF16
board and so, in turn, is missing the feed throughs on the front and back panels.

\begin{figure}[H]
\centering

\caption{Completed RFSoC Digitizer Module}
\label{fig:Enclosure_above}
\end{figure}

\begin{figure}[H]
\centering

\caption{Mostly Completed RFSoC Digitizer Module from the Front}
\label{fig:Front_completed}
\end{figure}

\begin{figure}[H]
\centering

\caption{Mostly Completed RFSoC Digitizer Module from the Back}
\label{fig:Back_complete}
\end{figure}

\begin{figure}[H]
\centering
s
\caption{Completed RFSoC Digitizer Module Installed in Signal Processing Room. Attemplifier Modules are also pictured. The RFSoC Digitizer Modules are the first and third modules from the bottom.}
\label{fig:Enclosure_in_Rack}
\end{figure}

\newpage

%----------------------------------------------------------------------------------------
%	Appendix A: RFSoC Enclosure Drawings
%----------------------------------------------------------------------------------------

\appendix
% ----------------------------------------------------------------

\includepdf[pages=-, landscape=true]{PDFs/24567174_05 (copy).pdf}
\includepdf[pages=-, landscape=true]{PDFs/24567174_98.pdf}
\includepdf[pages=-, landscape=true]{PDFs/24567174_99.pdf}
\includepdf[pages=-, landscape=true]{PDFs/24567174_100.pdf}

%----------------------------------------------------------------------------------------
%	Appendix B: RFSoC Digitizer Module Component List
%----------------------------------------------------------------------------------------
\begin{landscape}
\section*{B \hspace{.5cm} Component List of RFSoC Digitizer Module}

% ----------------------------------------------------------------

\begin{table}[H]
\centering
\resizebox{1.5\textwidth}{!}{%
\begin{tabular}{@{}lllllll@{}}
\toprule
Qty & Unit & Description & Manufacturer & PN Manufacturer & Distributor & PN Distributor\\
\midrule
1 & Each & EuropacPRO kit, heavy design, shielded, with front handles & Schroff & 
24567-174 & Distrelec & 110-74-433\\
1 & Each & 19" AC/DC switch-mode PSUs, maxpower 180 W, single 12V 13A & Schroff & 13100-151 & Distrelec & 110-89-774\\
1 & Each & Front Panel 13100 SLE 19" AC/DC Switch-Mode PSUs 128.4 mm, nVent Schroff & Schroff & 31006-677 & Distrelec & 110-90-375\\
1 & Each & Coding, PU 10 pack & Schroff & 20800-042  & Distrelec & 110-89-865\\
1 & Pack & Guide Rail Standard Type, Red, 160mm, Pack of 10 pieces & Schroff & 24568-361 & Distrelec & 302-25-177\\
1 & Each & Connector H 15 F, FASTON connection & Schroff & 69001-733 & Distrelec & 110-90-542\\
1 & Each & Front Panel & Front Panel Express, LLC & ATA-AP-24567174\_98.fpd\\
1 & Each & Rear Panel & Front Panel Express, LLC  & ATA-AP-24567174\_05.fpd\\
1 & Each & Baseplate & Front Panel Express, LLC & ATA-AP-24567174\_99.fpd\\
1 & Each & Cable Clamp & Front Panel Express, LLC  & ATA-AP-24567174\_100.fpd\\
1 & Each & DC Fans DC Fan, High Airflow Series, 80x80 & Sunon & PF80251V1-1000U-A99  & Mouser & 369-PF80251V11UA99\\
6 & Each & Axial Fan, IP20, 12 V, DC, 40 mm, 10 mm & EBM-PAPST & 412FM & Mouser & 5912-412FM\\
1 & Each & Fan Blower, GB Series, Compact, 12 V, DC & SUNON & GB1205PKV1-8AY.GN & Mouser & 369-GB1205PKV18AYGN\\
1 & Pack & Screw, SLT, CSK, Steel, BZP, M3X16 & TR Fastenings & M316 KSSTMCZ100- & Newark & 53M8739\\ 
1 & Pack & Enclosure Accessory, Grey, Plastic Sleeve & Schroff & 21100-464 & Newark & 74M6491\\
1 & Pack & 21101-101 -  COLLAR SCREW, PK100 & Schroff & 21101-101 & Newark & 74M6493\\
1 & Each & 4304.4005 -  INLET FILTER, IEC, C14, FKH, 10A & Schurter & 43044005 & Newark & 83T7492\\
6 & Each & Standoffs \& Spacers M3 x 25mm HEX & Harwin  & R30-3002502 & Mouser & 855-R30-3002502\\
25 & Each & Standoffs, Hex Male-Female, 20MM, M2.5 & RAF & M2115-2545-AL & Mouser & 761-M2115-2545-AL\\
1 & Each & DIN rail perforated & Phoenix Contact & 801733 & Mouser & 651-0801733\\
1 & Each & DIN Rail Terminal Blocks PTFIX 12X2,5-NS35ARD 2.5mm2  & Phoenix Contact & 3273158 & Mouser & 651-3273158\\
1 & Each & DIN Rail Terminal Blocks PTFIX 12X2,5-NS35ABK 2.5mm2 & Phoenix Contact & 3273168 & Mouser & 651-3273168\\
1 & Each & Headers \& Wire Housings 6CKT RECPT HSG & Molex & 45559-0002 & Mouser & 538-45559-0002\\
100 & Each & Headers \& Wire Housings MF PLUS HCS CRIMP TE RM. FEM 18-20 GA TIN & Molex & 45750-1112 & Mouser & 538-45750-1112\\
1 & Each & Extraction, Removal \& Insertion Tools EXTRACTION TOOL & Molex & 11-03-0044 & Mouser & 538-11-03-0044\\
1 & Each & Crimpers / Crimping Tools MINI-FIT 18-24AWG HAND TOOL & Molex & 63819-0901 & Mouser & 538-63819-0901\\
16 & Each & SMA Female Bulkhead to SSMC Plug Cable 18 Inch Length Using PE-SR405FLJ Coax & Pasternack & PE3C4448-18 & Pasternack & PE3C4448-18\\
1 & Each & SMA Female Bulkhead to MCX Plug Right Angle Semi-Flexible Precision Cable 18 Inch Length Using PE-SR405FLJ Coax, LF Solder, RoHS & Pasternack & PE39435-18 & Pasternack & PE39435-18\\
1 & Each & SMA Female Bulkhead to SSMC Plug Right Angle Cable 18 Inch Length Using PE-SR405FLJ Coax & Pasternack & PE3C4486-18 & Pasternack & PE3C4486-18\\
5 & Each & LED Panel Mount Indicator, Blue, 3.8 VDC, 6 mm, 20 mA & APEM & Q6F7BXXB02E & Mouser & 642-Q6F7BXXB02E\\
2 & Pack & SCREW,SECURITY FIXING, M2,5X5, PK100 & VERO & 173-202579H & Newark & 25M0782\\
1 & Pack & Machine Screw, M3, 25 mm & & & Newark & 27AC4115\\
2 & Each & Fuse, Cartridge, Slow Blow, 2 A, 250 V & Littlefuse & 0239002.HXP & Newark & 26K8412\\

\bottomrule            
\end{tabular}}
\label{tab:Interface_components}
\end{table}

\newpage

%----------------------------------------------------------------------------------------
%	Appendix C: Interface Board and HTG-ZRF16 board Component List
%----------------------------------------------------------------------------------------

\section*{C \hspace{.5cm} Interface Board and HTG-ZRF16 board Component List}

% ----------------------------------------------------------------

\begin{table}[H]
\centering
\resizebox{1.5\textwidth}{!}{%
\begin{tabular}{@{}lllllll@{}}
\toprule
Qty & Unit & Description & Manufacturer & PN Manufacturer & Distributor & PN Distributor\\
\midrule

1 & Each & ATA\_HTG\_ZRF16\_GPIO\_Board\_AP\_V1.0 & AP\\
1 & Each & PCB V1.0 & AP & ATA\_HTG\_ZRF16\_GPIO\_Board\_AP\_V1.0.zip\\
1 & Each & Littelfuse 1A T Non-Resettable Surface Mount Fuse, 125 V & Littlefuse & 0154001.DRT & Mouser & 576-0154001.DRT\\
1 & Each & Fuse, Surface Mount, 1.5 A, NANO 452 Series, 125 VAC, 32 VDC, Time Delay, SMD & Littlefuse & 045201.5MRL & Mouser & 576-045201.5MRL\\
1 & Each & Surface Mount Tantalum Capacitor, $100 \mu F$, 25 V, 2917 [7343 Metric], T491 Series, $\pm 10\%, -55 \degree C$ & Kemet & T491X107K025AT & Mouser & 80-T491X107K025AT\\
1 & Each & Electrolytic Capacitor, 220 $\mu F$, 35 V, M Series, $\pm 20\%$, Radial Leaded, 8 mm & PANASONIC & ECA-1VM221 & Mouser & 667-ECA-1VM221\\
1 & Each & KEMET C0805C224K1RACTU 220nF Multilayer Ceramic Capacitor MLCC 100V dc $\pm 10\%$ Tolerance SMD & Kemet & C0805C224K1RACTU & Mouser & 80-C0805C224K1R\\
1 & Each & KEMET C0805C104K5RACTU 100nF Multilayer Ceramic Capacitor MLCC 50V dc $\pm 10\%$ Tolerance SMD & Kemet & C0805C104K5RACTU & Mouser & 80-C0805C104K5R\\
1 & Each &  LINEAR VOLT REG, 5V, 1.5A, TO-263-3 & Texas Instruments & LM340SX-5.0/NOPB & Mouser & 926-LM340SX-5.0/NOPB\\
5 & Each & LED, QuasarBrite, Green, SMD, 1206, 20 mA, 2.2 V, 565 nm & LUMEX & SML-LX1206GW-TR  & Mouser & 696-SML-LX1206GW\\
6 & Each & LED, QuasarBrite, Yellow, SMD, 1206, 20 mA, 2 V, 590 nm & LUMEX & SML-LX1206SYC-TR & Mouser & 696-SML-LX1206SYC\\
1 & Each & Thin Film Resistors - SMD 0805 523ohm & Panasonic & ERA-6AEB5230V & Mouser & 667-ERA-6AEB5230V\\
18 & Each & Thin Film Resistors - SMD 0805 150ohms & Panasonic & ERA-6AEB151V & Mouser & 667-ERA-6AEB151V\\
1 & Each & Thin Film Resistors - SMD 0805 374ohm  & Panasonic & ERA-6AEB3740V & Mouser & 667-ERA-6AEB3740V\\
1 & Each & Thin Film Resistors - SMD 0805 1.07Kohm  & Panasonic & ERA-6AEB1071V & Mouser & 667-ERA-6AEB1071V\\
6(12) & Each & Thin Film Resistors - SMD 0805 200ohm & Panasonic & ERA-6AEB201V & Mouser & 667-ERA-6AEB201V\\
8 & Each & Thin Film Resistors - SMD 0805 4.7Kohms & Panasonic & ERA6AEB472V & Mouser & 667-ERA-6AEB472V\\
2 & Each & Optocoupler, Transistor Output, 4 Channel, DIP, 16 Pins, 60 mA, 5.3 kV, 100\% & VISHAY & ILQ2 & Mouser & 782-ILQ2\\
16 & Each & Buffers \& Line Drivers Single Schmitt-Trigger Buffer 5-SC70 -40 to 85 & Texas Instruments & SN74LVC1G17DCK3 & Mouser & 595-SN74LVC1G17DCK3\\
1 & Each & DIP Switches / SIP Switches SLIDE ACT 2 POS & Diptronics & NDS-02V & Mouser & 113-NDS-02V\\
1 & Each &  COMBICON MCV, 3.81mm Pitch, 2 Way, 1 Row, Straight PCB Terminal Block Header & Phoenix Contact & 1803426 & Mouser & 651-1803426\\
1 & Each & 2 way cable mount screw terminal, 3.81mm & Phoenix Contact & 1803578 & Mouser & 651-1803578\\
1 & Each & Headers \& Wire Housings 2.54mm CGrid Hdr Shr d /Slt .76AuLF 16Ckt & Molex & 70246-1602 & Mouser & 538-70246-1602\\
1 & Each & Headers \& Wire Housings 3CKT BRKWY HDR & Molex & 42375-1856 & Mouser & 538-42375-1856\\
8 & Each & Headers \& Wire Housings 2CKT BRKWY HDR & Molex & 42375-2486 & Mouser & 538-42375-2486\\
1 & Each & Ribbon Cables / IDC Cables 16Ckt & Samtec & IDSD-08-D-06.00 & Mouser & 200-IDSD08D0600\\
1 & Each & Headers \& Wire Housings 3 PIN SIL HOUSING & Harwin & M20-1060300 & Mouser & 855-M20-1060300\\
8 & Each & Headers \& Wire Housings 2 PIN SIL HOUSING & Harwin & M20-1060200 & Mouser & 855-M20-1060200\\
1 & Each & Headers \& Wire Housings F/M CRIMP TERM GOLD/TIN & Harwin & M20-1180042 & Mouser & 855-M20-1180042\\
1 & Each & Crimpers / Crimping Tools 2.54mm HAND CRIMP TOOL & Harwin & Z20-320 & Mouser & 855-Z20-320\\
1 & Each & Fan Tubeaxial 12VDC Square - 45mm L x 45mm H Ball 11.8 CFM (0.330m³/min) 2 Wire Leads & Delta Electronics & AFB04512HA & Digi-Key & 603-2157-ND\\
1 & Each & Heat Sink 45mm X 45mm X 24.5mm & Advanced Thermal Solutions & ATS-55450W-C1-R0 & Digi-Key & ATS1330-ND\\
2 & Each & Hex Standoff M2.5X0.45 Alum 20mm & RAF & M2115-2545-AL & Digi-Key & 1772-2060-ND\\
2 & Each & Mach Screw Pan Slotted M2.5X0.45 & Keystone Electronics & 29306 & Digi-Key & 36-29306-ND\\

\bottomrule            
\end{tabular}}
\label{tab:Attemp_components}
\end{table}

\newpage

%----------------------------------------------------------------------------------------
%	Appendix D: Interface Board Schematics
%----------------------------------------------------------------------------------------

\section*{D \hspace{.5cm} Interface Board Schematics}

% ----------------------------------------------------------------

%
\begin{figure}[H]
\centering

\caption{Interface Board Schematic Part 1}
\label{fig:interface_sch1}
\end{figure}
%

\end{landscape}

%
\begin{figure}[H]
\centering

\caption{Interface Board Schematic Part 2}
\label{fig:interface_sch2}
\end{figure}
%

%
\begin{figure}[H]
\centering

\caption{Interface Board Schematic Part 3}
\label{fig:interface_sch3}
\end{figure}
%

\end{document}

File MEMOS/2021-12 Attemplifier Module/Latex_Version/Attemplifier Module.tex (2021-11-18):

\documentclass[12pt,a4paper,oneside]{article}
\usepackage[margin=1.2in]{geometry}
\usepackage{appendix}
\usepackage[dvips]{graphicx}
\usepackage{epsfig}
\usepackage{amsmath}
\usepackage{amssymb}
\usepackage{psfrag}
\usepackage[square, comma,sort,numbers]{natbib}
\usepackage{fancyhdr}
\usepackage[nottoc]{tocbibind}
\usepackage{color}
\usepackage{fixltx2e}
\usepackage{pdfpages}
\usepackage{pdflscape}
\usepackage{booktabs}
\usepackage{graphicx}
\usepackage{float}
\usepackage{afterpage}
\usepackage{subcaption}
\usepackage{lscape}
\usepackage{rotating}
\usepackage{enumitem}
\usepackage{array,tabularx}
\usepackage{fancyref}
\usepackage[dvipsnames]{xcolor}
\usepackage[colorlinks=true,allcolors=blue]{hyperref}%

\newcommand{\quotes}[1]{``#1''}

\newenvironment{conditions*}
  {\par\vspace{\abovedisplayskip}\noindent
   \tabularx{\columnwidth}{>{$}l<{$} @{\ : } >{\raggedright\arraybackslash}X}}
  {\endtabularx\par\vspace{\belowdisplayskip}}

\pagestyle{fancy}
\title{\Huge The Hat Creek Radio Observatory\\
\vspace{0.5cm}
The Attemplifier Module\\
\vspace{0.5cm}
\normalsize \emph{}
\vspace{3.5cm}
\begin{center}

\end{center}
}
\author{ 
\vspace{1cm}
\Large
\textbf{ Alexander Pollak \& Sarah Schoultz} \\
SETI Institute \\ 
189 Bernardo Ave, Suite 200 \\
Mountain View, CA 94043 \\ 
Alexander.Pollak.87@gmail.com\\
}
\date{\today}

\begin{document}
\clearpage\maketitle
\thispagestyle{empty}

%\newpage
%\thispagestyle{empty}
%\section*{Abstract}
%\noindent 
%

%
%\vspace{3cm}
%\begin{flushright}
%Alexander Pollak \\ \emph{September, 2015}
%\end{flushright}

%\newpage
%\thispagestyle{empty}
%\tableofcontents
\newpage

%----------------------------------------------------------------------------------------
%	General
%----------------------------------------------------------------------------------------
%\pagestyle{plain}
\section{General}
\label{sec:1}
% ----------------------------------------------------------------

This document outlines general information regarding the Attemplifier Module such as the design, parts, wiring, cabling, and testing. This information is aimed at detailing the entire process of creating an Attemplifier Module from design to manufacturing to testing. 

The attmplifiers in the module condition the power level going into the analog to digital converter (an RFSoC) to the correct value. The module itself is needed to contain and operate sixteen attemplifiers as the digitizer, an HTG-ZRF16 board by High Tech Global, being used has sixteen channels. 

Finally, please note that \emph{this module can only be operated at 110V AC.} 

%----------------------------------------------------------------------------------------
%	CAD Design and Drawings
%--------------------------------------------------------------------------------------

\section{CAD Design and Drawings}
\label{sec:2}
% ----------------------------------------------------------------
This section includes a description of the CAD design. An image of the CAD model is shown in Figure 1. One can see the internal arrangement of the control board (left rear), general power supply (front right), the Raspberry Pi power supply (middle right) the Raspberry Pi (middle rear), the two layered racks of attemplifiers (middle), and directional fan (left rear). Note that the Raspberry Pi power supply, metal case perforated with circles, is not visible in Figure \ref{fig:CAD-Iso} but is in Figure \ref{fig:CAD-above}. The lid of the enclosure, not shown in Figure \ref{fig:CAD-Iso} or \ref{fig:CAD-above}, is perforated to further increase cooling. The panel facing the viewer in Figure \ref{fig:CAD-Iso} is considered the front panel. This is important to note for future sections. The majority of the Attemplifier Module enclosure is off the shelf (PN: 24563-174) except for a few parts: the front panel, the back panel, the base plate, and the attemplifier mounting rails. These custom parts were made by Front Panel Express, and the drawings can be found in Appendix A. 

\hfill \break

%
\begin{figure}[H]
\centering

\caption{ISO view of the Attemplifier Module CAD}
\label{fig:CAD-Iso}
\end{figure}
%

%
\begin{figure}[H]
\centering

\caption{Top View of the Attemplifier Module CAD}
\label{fig:CAD-above}
\end{figure}
%

For a part list of the Attmplifier Module, except for the attmplifiers,  control board, and some wiring parts, see Appendix B. 

%----------------------------------------------------------------------------------------
%	Control Board
%--------------------------------------------------------------------------------------

\section{Control Board}
\label{sec:3}
% ----------------------------------------------------------------

The control board is designed as an interface between the GPIOs of the Raspberry Pi and the attemplifiers. Assembled in house, see Figure \ref{fig:Control Board} for how a completed control board should look. A list of all the required parts for it appears in Appendix C. 

%
\begin{figure}[H]
\centering

\caption{Completed Control Board}
\label{fig:Control Board}
\end{figure}
%

\subsection{Design}
\label{sec:3.1}
% ----------------------------------------------------------------

The control board electrically isolates any signals from the Raspberry Pi via optocouplers to avoid any noise contamination. The board also includes two linear voltage regulators each of which powers eight attemplifiers. The board is designed to accept 9-25V DC as an input and includes several green LEDs indicating the supply voltage of the attemplifiers and control voltage of the board. Additionally, when programming an attemplifier, the control board shows the communication signals, clock, data, latch enable, using three yellow LEDs. Both the green and yellow LEDs showing the supply voltages and communication signals are duplicated on the front panel of the module and are connected to the control board via pin-headers. All of these functionalities are reflected in the schematic, Appendix D, and layout, Figure \ref{fig:Control_Layout} of the control board. The control board voltage range is 9-25V.

%
\begin{figure}[H]
\centering

\caption{Control Board Layout}
\label{fig:Control_Layout}
\end{figure}
%

%----------------------------------------------------------------------------------------
%	Attemplifiers
%--------------------------------------------------------------------------------------

\section{Attemplifiers}
\label{sec:4}
% ----------------------------------------------------------------

The purpose to the attemplifiers is to set the IF power level so that the ADCs operate with enough dynamic range and utilize the appropriate amount of bits.

\subsection{Design}
\label{sec:4.1}
% ----------------------------------------------------------------

Originally designed in 2007, the attemplifier's worked in conjunction with the IBobs. However, the IBobs have since been retired and replaced with the SNAP board and RFSOC Modules. Furthermore, 2007 attemplifier design was improved upon, and so the design that is used for the Attempifier Module is from 2012 and is called 1050-A. Figure \ref{fig:Attemp_Schem} and \ref{fig:Attemp_layout} show the electronic schematic and layout of 1050-A. For the amplifier enclosure design, go to Appendix E.

%
\begin{figure}[H]
\centering

\caption{1050-A Attemplifier Electronics Schematic}
\label{fig:Attemp_Schem}
\end{figure}
%

%
\begin{figure}[H]
\centering

\caption{1050-A Attemplifier Layout}
\label{fig:Attemp_layout}
\end{figure}
%

\subsection{Wiring}
\label{sec:4.2}
% ----------------------------------------------------------------

There are four 28 awg, twisted wire pairs connected to each attemplifier as shown in Figure \ref{fig:Attemplifier} and \ref{fig:Attemp_pegs}. One wire in each twisted pair is black and functions as the ground for the wire it is twisted with. 

%
\begin{figure}[H]
\centering

\caption{Attemplifier Complete with Wiring }
\label{fig:Attemplifier}
\end{figure}
%

%
\begin{figure}[H]
\centering

\caption{Soldered Wire Connection of an Attemplifier}
\label{fig:Attemp_pegs}
\end{figure}
%

The function of the other four wires is shown in Table \ref{table: Wire_func}. The ground wires are all soldered into a \#6 eye terminal which is screwed into the attemplifier (Figure \ref{fig:Attemp_pegs}). The other wires, meanwhile, are  soldered onto the attemplifier's feed through filters. The order in which they are soldered is shown in Figure \ref{fig:Attemp_pegs}. Note that the wire, solder, and eye terminal for the attemplifiers is considered on hand supplies and therefore are not listed in either of the component lists. 

\begin{table}[H]
\centering
\caption{Attemplifier Wire Functions}
\begin{tabular}{@{}cc@{}}
\toprule
Color & Function\\ 
\midrule
Yellow & Clock\\
White & Data\\
Green & Latch Enable\\
Red & Power\\

\bottomrule            
\end{tabular}
\label{table: Wire_func}
\end{table}

Each of the eight wires ends in a DF11 series crimped contact (PN: DF11-2428SC) that are all then inserted into a DF11 series wire to board header connector (PN: DF11-10DP-2DSA(24)). Figure \ref{fig:pinout} shows the pin out of this connector as viewed from the mating face. The black wire from each twisted pair is directly below its partner in the connector.

%
\begin{figure}[H]
\centering

\caption{Connector Pin Out of an Attemplifier}
\label{fig:pinout}
\end{figure}
%

\subsection{Testing}
\label{sec:4.3}
% ----------------------------------------------------------------

The attemplifiers were manufactured far prior to the Attemplifier Module being designed. Therefore, before installation, all 352 attemplifiers were tested. The test setup required a N5230C VNA, two male to male SMA cables, female to female adapter, a Raspberry Pi 2 Model B, a control board, a 40 to 40 GPIO Ribbon Cable, a power supply and connector for the Raspberry Pi, a power supply and connector for the control board. Note that the control board's voltage range is 9-25V. To set up the test, the VNA's power is set to -10dBm and the frequency to 10MHz-2GHz.  Then one SMA needs to connected to Port 1 of the VNA on one end and the other to the female terminal on the attemplifer. Next, the second SMA needs to be connected to the VNA's Port 2 and the male terminal on the attemplifier with the female to female adapter in between. Power up the Raspberry Pi and control board and connect them via the 40 to 40 GPIO Ribbon Cable. Finally, plug the attemplifier into P1 of the control board. An image of this test setup is shown in Figure \ref{fig:Attemp_test}. 

%
\begin{figure}[H]
\centering

\caption{Set Up to Testing of Indivual Attemplifiers}
\label{fig:Attemp_test}
\end{figure}
%

Commands can now be given through a terminal to set the attenuation of the attmplifier to different values using a script called TestRun. These attenuation changes are displayed on the VNA to show whether the attemplifier is functioning. Below are step-by-step directions on how to test an attemplifier.

\begin{enumerate}
 \item ssh into the Raspberry Pi: ssh sonata@10.1.49.230
 \item Run TestRun script
 \item Watch how the graph on the VNA responds as the attenuation increases. Figure \ref{fig:Test_Run} shows how the VNA display should look as TestRun sets the attenuation to 0dB, 1dB, 2dB, 4dB, 8dB, and 16dB.  Graphs a-f from Figure \ref{fig:Test_Run} match the attenuation settings in ascending order. 

 \item Rate the Attemplifier as pass or fail based on whether its VNA graphs were correct
 
\end{enumerate}

\begin{figure}[H]
 \centering
 
 \begin{subfigure}[b]{.6\linewidth}
   
   \caption{}
   \label{fig:test_0dB}
 \end{subfigure}
 
 \begin{subfigure}[b]{.6\linewidth}
  \centering
   
   \caption{}
   \label{fig:test_1dB}
 \end{subfigure}
 
 \begin{subfigure}[b]{.6\linewidth}
  \centering
  
  \caption{}
  \label{fig:test_2dB}
 \end{subfigure}

\end{figure}
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

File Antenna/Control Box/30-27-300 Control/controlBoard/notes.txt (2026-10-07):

Same board as rim controller, but that needs the corner populated.

From Rob's e-mail:
CadSoft Eagle board file (AlidadeEEBoxuCntrlr.brd) and PCB Gerber layout and drill files (AlidadeEEBoxuCntrlr.zip) attached.

Schematic is not yet available.

Contents of ZIP file (AlidadeEEBoxuCntrlr.zip):

AlidadeEEBoxuCntrlr.drd - drill file (center position of holes)
AlidadeEEBoxuCntrlr.dri - drill info (references drd and drl)
AlidadeEEBoxuCntrlr.drl - drill tool list (drill sizes)
AlidadeEEBoxuCntrlr.L1 - top layer
AlidadeEEBoxuCntrlr.L2 - second to top layer
AlidadeEEBoxuCntrlr.L3 - third to top layer
AlidadeEEBoxuCntrlr.L4 - third to bottom layer
AlidadeEEBoxuCntrlr.L5 - second to bottom layer
AlidadeEEBoxuCntrlr.L6 - bottom layer
AlidadeEEBoxuCntrlr.oln - board outline and mounting holes
AlidadeEEBoxuCntrlr.slk - top silkscreen
AlidadeEEBoxuCntrlr.smb - bottom solder mask
AlidadeEEBoxuCntrlr.smt - top solder mask

units are imperial (inches) not metric!

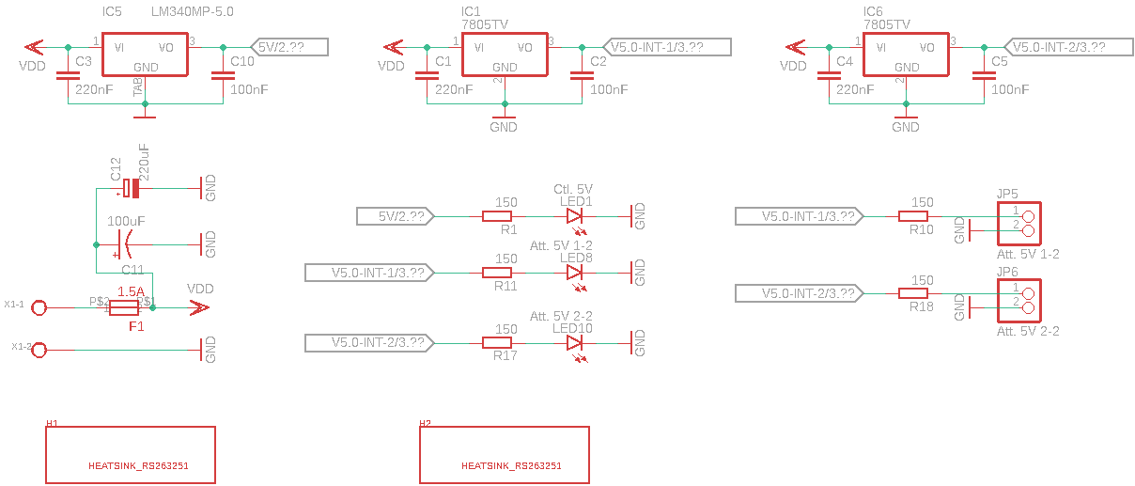
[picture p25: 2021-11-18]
MEMOS/2021-12 Attemplifier Module/Latex_Version/figures/control_board_schematic_1.png

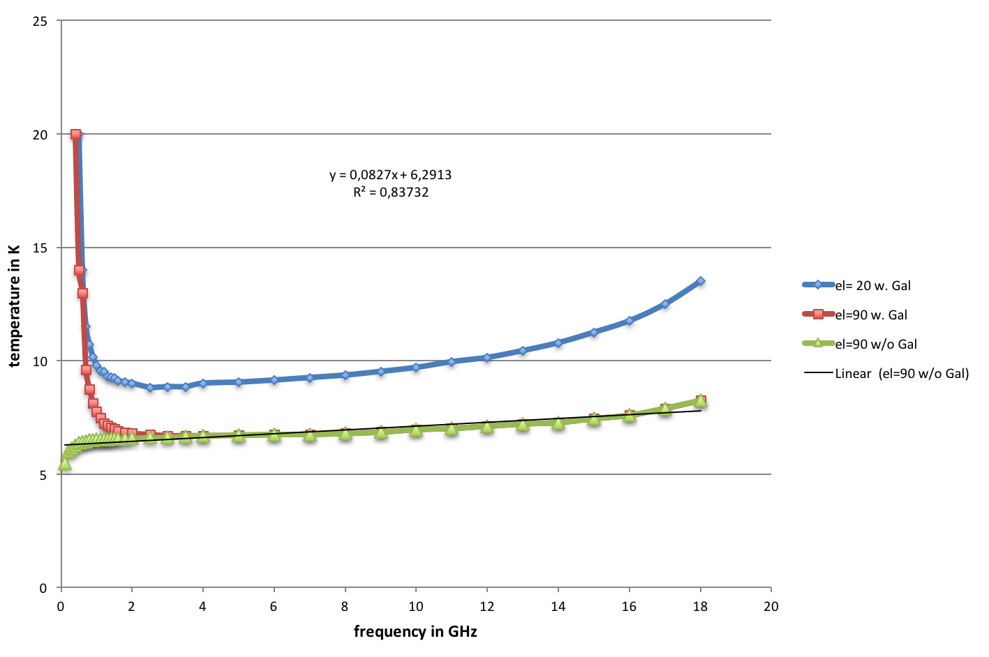
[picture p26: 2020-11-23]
Antonio-Feed/Feed Inspections/Report/figures/sky-model.png

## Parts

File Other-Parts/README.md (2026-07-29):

This repo contains mechanical drawings, assemblies, and part files for miscellaneous projects around Hat Creek Radio Observatory. Parts created with AutoDesk Inventor 2024/25 and Front Panel Designer.

## Index

### GOES Antenna Mount
Custom mount for [Nooelec GOES grid antenna](https://www.amazon.com/gp/product/B08HGQXC7C/ref=as_li_ss_tl?smid=A2JO7YP9I9Y3D6&psc=1&linkCode=sl1&tag=rsv0f-20&linkId=0e1541f0a7610de1997e308c836bce88&language=en_US) used in ARISE Lab [Decoding Earth](https://agiseti.com/index.html).

### HCRO ALPACA Shed
Documents relating to construction of the shed that houses [ALPACA](https://gitlab.ras.byu.edu/alpaca/homepage).

### PCB Holder
Small plate to hold [PAX PCBs](https://github.com/SETIatHCRO/Front-Page/tree/master/Analog-Signal-Components/PAX/PAM-2025) within stencil frame fixture for solder paste application.

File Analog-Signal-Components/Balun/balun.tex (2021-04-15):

Tapered microstrip balun for ATA feed development
G. Engargiola

Abstract:

Introduction:

The current design of the ATA feed is a non-planar
log-periodic antenna with a 20 degree opening angle. Between the
arms of the antenna is located a square pyramidal metallic shield
with a 10 degree opening angle, which serves as a vacuum container 
for a cryogenic amplifier. The self-similar geometry of
the antenna/shield combination produces a radiation pattern and
impedance which vary insignificantly over a log period in
frequency. A connection from the balanced leads of the antenna
to the electronics interior to the shield can be made in two ways:
Each antenna arm can be connected via an unbalanced transmission
line to an independant unbalanced amplifier input. Opposite antenna
arms produce antisymmetric signals, hence their amplified outputs
can be combined with a 180 degree hybrid; a scheme for this connection
is described in a separate memo. Alternatively, the balanced terminals
of the antenna can be connected via a balun to a single amplifier.
The balun must be appropriately broadband, matching the terminal
impedance of the antenna to the amplifier input, and compatible with
the long narrow geometry of the shield at the location of the
antenna terminals. I present a design for such a balun in this memo.

Basic design:

Simply put, a balun is a reciprocal transducer, converting the odd signal
mode at the antenna terminals to the sum of an odd and even mode 
at the terminals of an unbalanced (grounded) transmission line structure.
In effect, it passes microwave energy while blocking net rf current
flow between the two ports. Space contraints in the pyramidal
shield and the need for wide bandwidth make a taperline design ideal --
ferrite core baluns are too bulky and narrowband.

The opening of the pyramidal shield is 150 x 150 mil at the feed terminals,
which are separated by 300 mil. Moreover, since two orthogonal non-planar
LP antennas surround the pyramidal shield for dual polarization,
the balanced ports of two baluns must be brought to the narrow tip of
the shield without inducing significant cross-polarization coupling. For this
reason, the shield volume must be partitioned by a metallic septum,
so that the baluns do not capacitively couple.

Figure 2 shows the tip of the dual polarization feed structures.
The shield volume is partitioned diagonally so that the balanced
port of each balun can be located to give maximum separation from
the surrounding grounded metal walls, which limits the highest
practical impedance on can achieve with a twin-lead type
transmission line. The balanced port of each balun must
must have the same impedance as the antenna terminals (240 ohms).
This can be conveniently achieved within the available space contraints
by fabricating offset 10 mil microstrip lines separated by 50 mil
on opposite sides of 15 mil thick Cuflon.
The balun leads are approximately 50 mils equidistant from the
septum and pyramidal
shield walls.

The twin-lead input of the balun must also be a 250/50 ohm transition
section. The input of the balun transducer section is a broadside-coupled
stripline pair; it is most conveniently mated to the 240 ohm twin
leads by asymmetrically tapering top and bottom conductors (fig 3a)
so that the outer diameter of the pair remain constant (60 mil).
The cross section
of our impedance matching twin-lead is shown in fig. 3b.
An IE3D simulation gives the impedance of this transmission line structure
as a function of a single linear parameter x (see fig 4). The 
impedance steps yield a 20-section 240/50 ohm transformer of minimum
length with a 
25 dB return loss (Klopfenstein taper). The number of steps limits
the upper frequency cutoff (> 10 GHz) and the total length determines
the low frequency cutoff (< 1 GHz). 

The transducer section consists of line conductor of nearly constant width 
(60 mil) broadside coupled through Cuflon substrate to a line which is
identical in width at the balanced port, then flares out exponentially (fig 5).
At the unbalanced port, the balun transducer is effectively a microstrip
line, where the bottom conductor becomes the ground plane (it is attached to
case ground along the end). The length
of the transducer and speed of the taper of the bottom conductor line
determine the passband of
the transducer section, which I optimized for 1 - 10 GHz.    

Test Results:

As shown in Fig 1 this taperline balun has two sections, the balanced
line portion which matches the antenna impedance to ~50 ohms and
a portion which actually performs the mode transduction.
One method to confirm the proper function of this balun design is
to connect two, end-to-end, at the balanced port (see fig. 6).
Clearly, the center of this circuit arrangement is a balanced twin lead
while the ends, which are microstrip-to-coax transitions, are
unbalanced. Figure 7 shows the transmission properties of this
circuit at room temperature are excellent: |S21| = 0.5 -- 0.8 dB
for freq. = 1 -- 1 GHz. Gating out reflections from the SMA
connectors, return loss from the transducer and impedance
matching sections is 20 -- 30 dB across the band of operation.
To check the phase performance of the balun circuit, a second
circuit is made by connecting two, end-to-end, as before, but with
the twin leads cross-connected. Since the balun transforms
a balanced signal in the E-plane to an unbalanced signal in the
H-plane, a comparison of our two back-to-back balun pairs should
exhibit a 180 degree phase difference over the passband. Figure 8
shows that this is indeed the case from 1 - 10 GHz. Phase errors
of only a few degrees occur over this frequency range.

Discussion:

The results previously quoted were for balun pairs mounted
in an open test fixture. For the balun to function properly, it must
work in a pyramidal shield. The effects of nearby conducting
walls are two-fold: they lower the characteristic impedance of both balanced
and unbalance transmission lines, making them more lossy;
they provide a conduction path 
for in-phase signals (the even mode) along twin leads.
At the tip of the pyramidal shield, the impedance of the balanced
transmission line mode (odd mode) and the even mode are 240 ohms
and 120 ohms respectively. Because the shield flares out at a 5 degree
half-angle, the impedance of the even mode continuously increases
from 120 ohms at the balanced port to 1K ohm at the unbalanced
port according to full wave simulations of the balun/shield combination,
hence the ratio of odd/even mode impedances is nearly 20:1. 
It is expected that with a good impedance match to the balun at
the unbalanced side the even mode excitation should be negligible.
In any case, this balun fabricated for Cuflon is certainly adequate for
range testing the ATA feed antenna patterns. Use of this balun
in a cryogenic front end requires scaling it to alumina, which means
reducing its length by more than a factor of 2, and making sure
significant excitation of the even mode does not occur, which can
raise the sidelobe patterns and make the beam profile asymmetric.
In table 1 I present the boundary design conditions and losses
if the alumina based circuit is cooled to 80 K.

One way to attenuate the even mode in an cryogenic balun is to attach 
a resistive card vane to the inside of the shield, perpendicular
to the cooled circuit board (see figure 9). Care must be taken not
to attenuate the odd mode in locations where the fringe fields
between balanced leads are high. To avoid this, th vane should probably 
have maximum extent at the balun "neck" where 60 mil lines are
broadside coupled and fringe fields are at minimum strength.

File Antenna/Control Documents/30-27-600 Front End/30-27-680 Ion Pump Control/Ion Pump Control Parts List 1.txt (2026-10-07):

EMCO high voltage Supply
	1KBUVBQ	DC to DC high voltage supply, Emco Mod: E50

LED Output, Fault, Fuse.		Dialight	( Mouser p )
	645-550-5107F	LED, CBI, 5mm, rt angle, red, super bright, slant back.
	645-550-5207F	LED, CBI, 5mm, rt angle, grn, super bright, slant back.
	645-550-5307F	LED, CBI, 5mm, rt angle, yel, super bright, slant back.

Reset button	E Switch  ( Mouser p1286 )
	612-TL1105SF160Q	Switch, tactile, rt ang, 8.35mm

Phono Jack for current reading	Kombiconn   ( Mouser p0921 )
	161-3505	Jack, 3.5mm, mono, PCB mount, D

Fuse Holder			Cooper Bussman    ( Mouser p0488 )
	504-HBH-I	Fuse holder, PCB 0.25 x 1.25.  ( or PTC resetable )

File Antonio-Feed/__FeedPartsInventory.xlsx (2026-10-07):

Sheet: Parts At ATA
Antenna Inventory
Ant | ControlBox | DriveBox | Feed | PaxBox | RFCB | Notes
1A (https://drive.google.com/open?id=1h79fqthLoRJDjhC2klnjbkG8MB2JL2Hy) | CB-0017 | DB-016 | SB-017 | PB-012 | RFCB-039
1B (https://drive.google.com/open?id=1OPl2VmHH1ZeMZjQWNCCkQkA6bOfyIeqj) | CB-0012 | DB-030 | 5C4-024 | PB-036
1C (https://drive.google.com/open?id=1_67Lwh4ATjaUkKTpdhqNA2vhhSxMhfoh) | CB-0045 | DB-025 | 5C4-019 | PB-040 | RFCB-040
1D (https://drive.google.com/open?id=1RDZathABUe1AxNllos18oBRUGkUw-BAb) | CB-0051 | DB-008 | 5C4-022 | PB-010
1E (https://drive.google.com/open?id=1B7jEgQfvgjZIKbfW8eR9qm2PDLYRcFFX) | CB-0006 | DB-039 | 5C4-015 | PB-033
1F (https://drive.google.com/open?id=1y8psJsldf8GOPKXdI3_7jAN-0VefmuVb) | CB-0138 | DB-027 | SB-039 | PB-022 | RFCB-042
1G (https://drive.google.com/open?id=1Ak0bagtonjeBe0T45ml7mh9V5vKH_FoI) | CB-0015 | DB-019 | 5C4-003 | PB-028
1H (https://drive.google.com/open?id=15tp_vGgbK5-4zzthz0W8wuq2zgKokja6) | CB-0044 | DB-041 | 5C4-013 | PB-039 | RFCB-027
1J (https://drive.google.com/open?id=1EMft8Du0dvrSSlstsShqV16Nnrlb4EO_) | CB-0111 | DB-0034
1K (https://drive.google.com/open?id=1B-AwkTkUdHQS0dThuP6mM5L_0XIFZ2QS) | CB-0046 | DB-038 | 5C4-012 | PB-026 | RFCB-029
2A (https://drive.google.com/open?id=1XILFfrJerwAeHeN4xKdQH-99VN9y0QS7) | CB-0028 | DB-020 | 5C4-005 | PB-013 | RFCB-032
2B (https://drive.google.com/open?id=1i7lErxBcw13LxRubiAB_0upxTGrTLBvi) | CB-0012 | DB-031 | 5C4-004 | PB-005 | RFCB-043
2C (https://drive.google.com/open?id=1HmSkhlRiy_w_xIcPrlD-Gu21Q1sHCajk) | CB-0018 | DB-033 | 5C4-010 | PB-034
2D (https://drive.google.com/open?id=1ih9AM9nSu6WpURV8EnXu6Q1HkOh5dSXM) | CB-0034 | DB-0002 | 5C4-025 | PB-001
2E (https://drive.google.com/open?id=1ilbwUzFLn2Zr9CQ_v673T9KjSALf_GzB) | CB-0010 | DB-035 | 5c4-014 | PB-029 | RFCB-037
2F (https://drive.google.com/open?id=1H2B7fJmOymk8ZeyITqVgqJIR9EbewGjs) | CB-0021 | DB-017 | 5C4-023 | PB-042
2G (https://drive.google.com/open?id=1GXDi1coA9HtIo5F2GTLcPhpAh_IiHrmJ) | CB-0101 | DB-045
2H (https://drive.google.com/open?id=18itspidwzvb4KFHkqj1122TxuhHxILwX) | CB-0050 | DB-022 | 5C4-002 | PB-006 | RFCB-035
2J (https://drive.google.com/open?id=12YgGEJrua5a-agu15lV4vezflw1cOjQ4) | CB-0016 | DB-009 | 5C4-011 | PB-045
2K (https://drive.google.com/open?id=1mdMrKj4CCNPy7BlChSDOU2hQAJONhZzU) | CB-0044 | DB-032 | 5C4-001 | PB-035
2L (https://drive.google.com/open?id=14mzIl-szkFL_WWXlsFZ9T_x3Mt5RAOn0) | CB-0046 | DB-012 | 5C4-018 | PB-027
2M (https://drive.google.com/open?id=1-X_VRvOqUUm_bcQ792NJw8TTxR5Kl3lr) | CB-0031 | DB-007 | 5C4-008 | PB-015
3C (https://drive.google.com/open?id=1ofYuI7zJYOx0Em5kOgymDe9L2TWaIZ-_) | CB-0022 | DB-004 | 5C4-020 | PB-016 | RFCB-048
3D (https://drive.google.com/open?id=1X9eTLHcdh-lSX2OXG4OLDNwPRG5eoz9l) | CB-0042 | DB-047 | 5C4-017 | PB-019
3E (https://drive.google.com/open?id=1m_ACLfEw9sFFcCd16wQnkI9wa3WI7gK9) | CB-0032 | DB-011
3F (https://drive.google.com/open?id=1CIBdXiHhWBrM6LwlY-yGooPill1DRTQ7) | - | - | - | - | -
3G (https://drive.google.com/open?id=1c2xmouFbs4cNAvpeHuAdgNreh8kFEC2V) | - | - | - | - | -
3H (https://drive.google.com/open?id=1t7wkFvS4sGjdMU60zYacdFSrl4pYayl_) | - | - | - | - | -
3J (https://drive.google.com/open?id=1N0-R1KTkpoZjXWmN7r0U_myR9XBY5SDj) | CB-0049 | DB-013
3L (https://drive.google.com/open?id=13pmWKIsTMFsSuBTJ-HZb5DVIowIXTS_s) | CB-0020 | DB-005 | 5C4-007 | PB-004 | RFCB-046
4E (https://drive.google.com/open?id=16nGNQgv2r19h9agxYjXmQ8rC4v330dYf) | CB-0136 | DB-0014 | 5C4-009 | PB-043
4F (https://drive.google.com/open?id=1bmJc7h6PrfobWHjtATEPhVDZqxi3ORaa) | CB-0113 | DB-0049
4G (https://drive.google.com/open?id=1nHAP6VZOPX4PWClDeQpEHh4MuzIQchEa) | CB-01 | DB-037 | SB-030 | PB-037 | RFCB-014
4H (https://drive.google.com/open?id=1a78u8iOyRFbuJtQlj9X51FknS9EfCDih) | CB-0124 | DB 0006
4J (https://drive.google.com/open?id=1zZjefBVzFC9BP-YmMKfQZMWa1XGkqomj) | CB-0009 | DB-010 | 5C4-006 | PB-008 | RFCB-024
4K (https://drive.google.com/open?id=1qWFlabv0TeVOBvOIJQuvHlR1H3AMOPvN) | CB-0002 | DB-046
4L (https://drive.google.com/open?id=176NV2NM9yvfuW1EMU3iBS768FxgmXjUS) | CB-0025 | DB-040
5B (https://drive.google.com/open?id=1cC0P-G66cPSNnf6v6z8opZCNyporo74Y) | CB-0029 | DB-043 | 5C4-016 | PB-024
5C (https://drive.google.com/open?id=1q_N74b1OZrCze7zuXy5fm0ASU07tWzh3) | CB-0100 | DB-018 | SB-038 | PB-031 | RFCB-031
5E (https://drive.google.com/open?id=1aKSCelAY002Ihje9mdJi7jFh0OB4j8XZ) | CB-0039 | DB-029 | 5C4-021 | PB-002
5G (https://drive.google.com/open?id=1ghdX_COwJq4oYlhj-qYPypK_2GlrWyQZ) | CB-0052 | DB-024
5H (https://drive.google.com/open?id=1MR24L4GDI5x861k8SMrgm71xRfm55Hiv) | CB-0114 | DB-028

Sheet: Feed Retrofit Overview
Feed List |  | Feed Revision Overview
Number | Installed Ant. | Tip-Link: R03 | Temp S. Isolation | New Harness | Bellow Removed | Cryo Tuned | Firmware 5.4 | Gold-Plated | Preconditioned Coax | PY Number
5C4-001 | 2K | x | x | x | x | x | x | x | x
5C4-002 (https://drive.google.com/drive/folders/1G8ecO5ODQmn8FX8jzQ962D928BpQ6iUm) | 2H | x | x | x | x | x | x | x | x
5C4-003 (https://drive.google.com/drive/folders/1X_yNido1T9NRAtsXoJ-h2bFXlpLfFW-N) | 1G | x | x | x | x | x | x | x | x
5C4-004 (https://drive.google.com/drive/folders/1WeIiiMAp6TYYdsybsr5MvXeiX_cVX9j0) | Feed Lab | x | x | x | x | x | x | x | x
5C4-005 (https://drive.google.com/drive/folders/1rFsrgDjf_nAuKofi6JoxLvoaGo8A4adh) | 1C |  |  |  |  |  |  |  |  | QRFH V2
5C4-006 (https://drive.google.com/drive/folders/1vHgkPcaz684Ip98C0QpWVB-bTK7EvvdW) | 4J | x | x | x | x | x | x | x | x
5C4-007 | 3L | x | x | x | x | x | x | x | x
5C4-008 (https://drive.google.com/drive/folders/1-3h2_HbCYYPIJxLORcasFd7NqbLvOw-C) | 2M | x | x | x | x | x | x | x | x
5C4-009 (https://drive.google.com/drive/folders/1EhIIjKRxAQ858Wo2OYQq3GdqbI2ok5Af) | 4E |  |  |  |  |  |  |  |  | QRFH V1
5C4-010 (https://drive.google.com/drive/folders/1FrnQUGPHDhAq4DHWLuBTTfQpLNsdUckc) | 2C | x | x | x | x | x | x | x | x
5C4-011 (https://drive.google.com/drive/folders/1hJ1DyO35m4DO0phNhkoobK76R8Ql-DTn) | 2J | x | x | x | x | x | x | x | x
5C4-012 (https://drive.google.com/drive/folders/1MyuBrs08Ryi2pvVUeI0hW4p24qsMsUL4) | Feed Lab | x | x | x | x | x | x | x | NA
5C4-013 (https://drive.google.com/drive/folders/19GonN6xbnfrGARLvh-LLFUsxF-EngP3u) | 1H | x | x | x | x | x | x | x | x
5C4-014 (https://drive.google.com/drive/folders/1LUZSYEAIfX8EFKKfjUSeyrC0JCfBfe8h) | 2E | x | x | x | x | x | x | x | x
5C4-015 (https://drive.google.com/drive/folders/1GhnG5G_BN5lBSXzegcxU-3TuUUTEd6xm) | 1E | x | x | x | x | x | x | x | x
5C4-016 | 5B | x | x | x | x | x | x | x | x
5C4-017 (https://drive.google.com/drive/folders/1wcHyiuVUbBeL9ODgyYP-lyy7yM1vMH3u) | 3D | x | x | x | x | x | x | x | x
5C4-018 | 2L | x | x | x | x | x | x | x | x
5C4-019 (https://drive.google.com/drive/folders/1x-FjLa7p2gJDSbRaODzjs8ijaA9SGLtW) | 2B | NA | x | x | x | x | NA | NA | NA
5C4-020 (https://drive.google.com/drive/folders/1wMVARUxnYHeiTbbEodCmZFb_vx9FkRVr) | 3C | x | x | x | x | x | x | x | x | 009
5C4-021 | 5E | x | x | x | x | x | x | x | x | 021
5C4-022 | 1D | x | x | x | x | x | x | x | x | 022
5C4-023 | 2F | x | x | x | x | x | x | x | x | 023
5C4-024 | 1B | x | x | x | x | x | x | x | x | 024
5C4-025 | 2D | x | x | x | x | x | x | x | x | 025
5C4-026 | FeedLab |  | x | x | x |  | x
5C4-027 | LAB1
5C4-028 | LAB1
5C4-029 | LAB1
5C4-030 | LAB1
5C4-031 | LAB1
5C4-032 | LAB1
5C4-033 | LAB1
5C4-034 | LAB1
5C4-035 | LAB1
5C4-036 | LAB1
5C4-037 | LAB1
5C4-038 | LAB1
5C4-039 | LAB1
5C4-040 | LAB1
5C4-041 | LAB1
5C4-042 | LAB1
5C4-043 | LAB1
5C4-044 | LAB1

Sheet: PY
Pyramid Overview
Number | LNA X | LNA Y | X-Y switched | Bias ID | Labeled
PY-001 | 50 | 71 | - | 25mA | YES
PY-002 | 55 | 62 | YES | 25mA | YES
PY-003 | 12 | 39 | - | 25mA | YES
PY-004 | 43 | 44 | - | 25mA | YES
PY-005 | 47 | 52 | - | 25mA | -
PY-006 | 75 | 82 | - | 25mA | -
PY-007 | 41 | 99 | - | 25mA | YES
PY-008 | 15 | 23 | YES | 25mA | YES
PY-009 | 19 | 21 |  | 25mA | YES
PY-010 | 24 | 73 | - | 25mA | YES
PY-011 | 57 | 59 | YES | 25mA | YES
PY-012 | 37 | 56 | - | 25mA | Yes
PY-013 | 53 | 72 | - | 25mA | -
PY-014 | 60 | 64 | - | 25mA | YES
PY-015 | 45 | 48 | - | 25mA | -
PY-016 | 16 | 17 | - | 25mA | YES
PY-017 | F66 | F67 | - | 60mA | YES
PY-018 | 18 | 40 | - | 25mA | -
PY-019 | 34 | 46 | - | 25mA | YES
PY-020 | 83 | 84 | - | 25mA | YES
PY-021 | F27 | F32 | - | 60mA | YES
PY-022 | F58 | F98 | - | 60mA | YES
PY-023 | F1 | F4 | - | 60mA | YES
PY-024 | 30 | 68 | - | 25mA | YES
PY-025 | 3 | 2 | - | 25mA | YES
QRFH V1 | 2064Z | 2287Z |  | 30mA |  | Vds=1.20V
QRFH V2 | 4270H | 4332H |  |  |  | Vds=1.20V

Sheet: Vibration Measurements
Feed List |  | Vibration Measurements
Number | Installed Ant. | Initial, before tuning | Tuned Value | Followup measurement | Followup tuned value
5C4-001 (https://drive.google.com/drive/folders/1G8ecO5ODQmn8FX8jzQ962D928BpQ6iUm) | 2K |  | X=0.06Y=0.08 Z=0.14
5C4-002 (https://drive.google.com/drive/folders/1G8ecO5ODQmn8FX8jzQ962D928BpQ6iUm) | 2H | X=0.23 Y=0.07 Z=0.22 | X=0.14 Y=0.06 Z=0.15
5C4-003 (https://drive.google.com/drive/folders/1X_yNido1T9NRAtsXoJ-h2bFXlpLfFW-N) | 1G | X=0.20 Y=0.07 Z=0.20 | X=0.05 Y=0.05 Z=0.12
5C4-004 (https://drive.google.com/drive/folders/1WeIiiMAp6TYYdsybsr5MvXeiX_cVX9j0) | 2B | X=0.09 Y=0.07 Z=0.26 | X=0.07 Y=0.04 Z=0.16
5C4-005 (https://drive.google.com/drive/folders/1rFsrgDjf_nAuKofi6JoxLvoaGo8A4adh) | 2A
5C4-006 (https://drive.google.com/drive/folders/1vHgkPcaz684Ip98C0QpWVB-bTK7EvvdW) | 4J |  | X=0.15 Y=0.13 Z=0.10
5C4-007 | 3L | X=0.15 Y=0.05 Z=0.38 | X=0.04 Y=0.05 Z=0.11 | X=0.22 Y=0.15 Z=0.28 | X=0.11 Y=0.10 Z=0.11
5C4-008 (https://drive.google.com/drive/folders/1-3h2_HbCYYPIJxLORcasFd7NqbLvOw-C) | 2M | X=0.19 Y=0.05 Z=0.18 | X=0.09 Y=0.04 Z=0.16
5C4-009 (https://drive.google.com/drive/folders/1EhIIjKRxAQ858Wo2OYQq3GdqbI2ok5Af) | 4E | X=0.13 Y=0.05 Z=0.14 | X=0.08 Y=0.04 Z=0.15
5C4-010 (https://drive.google.com/drive/folders/1FrnQUGPHDhAq4DHWLuBTTfQpLNsdUckc) | 2C | X=0.12 Y=0.04 Z=0.22 | X=0.08 Y=0.03 Z=0.15
5C4-011 (https://drive.google.com/drive/folders/1hJ1DyO35m4DO0phNhkoobK76R8Ql-DTn) | 2J | X=0.24 Y=0.05 Z=0.19 | X=0.07 Y=0.05 Z=0.16
5C4-012 (https://drive.google.com/drive/folders/1MyuBrs08Ryi2pvVUeI0hW4p24qsMsUL4) | 1K |  | X=0.32 Y=0.09 Z=0.14
5C4-013 (https://drive.google.com/drive/folders/19GonN6xbnfrGARLvh-LLFUsxF-EngP3u) | 1H |  | X=0.12 Y=0.06 Z=0.22
5C4-014 (https://drive.google.com/drive/folders/1LUZSYEAIfX8EFKKfjUSeyrC0JCfBfe8h) | 2E | X=0.37 Y=0.08 Z=0.19 | X=0.07 Y=0.03 Z=0.15
5C4-015 (https://drive.google.com/drive/folders/1GhnG5G_BN5lBSXzegcxU-3TuUUTEd6xm) | 1E | X=0.13 Y=0.05 Z=0.28 | X=0.07 Y=0.02 Z=0.12
5C4-016 | 5B | X=0.70 Y=0.04 Z=0.13 | X=0.05 Y=0.04 Z=0.14
5C4-017 (https://drive.google.com/drive/folders/1wcHyiuVUbBeL9ODgyYP-lyy7yM1vMH3u) | 3D | X=0.25 Y=0.05 Z=0.28 | X=0.18 Y=0.05 Z=0.20
5C4-018 | 2L | X=0.22 Y=0.08 Z=0.18 | X=0.11 Y=0.07 Z=0.11
5C4-019 (https://drive.google.com/drive/folders/1x-FjLa7p2gJDSbRaODzjs8ijaA9SGLtW) | 1C
5C4-020 (https://drive.google.com/drive/folders/1wMVARUxnYHeiTbbEodCmZFb_vx9FkRVr) | 3C | X=0.18 Y=0.05 Z=0.18 | X=0.12 Y=0.03 Z=0.09
5C4-021 | 5E
5C4-022 | 1D
5C4-023 | 2F
5C4-024 | 1B |  | X=0.15 Y=0.06 Z=0.15
5C4-025 | 2D
5C4-026 | Feed Lab | X=0.21 Y=0.10 Z=0.13 | X=0.07 Y=0.03 Z=0.10

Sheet: Antenna Retrofit
Antennas |  |  |  | Communication |  |  | Verfification
Ant | Feed Version | Feed installed | Control Box | Rim Box | Pax Box | Drive Box | AF retrofit 48V connector replacement
1A (https://drive.google.com/open?id=1h79fqthLoRJDjhC2klnjbkG8MB2JL2Hy) | V1 | YES | x | x | x | x | -
1B (https://drive.google.com/open?id=1OPl2VmHH1ZeMZjQWNCCkQkA6bOfyIeqj) | V2 | YES | x | x |  | x | x
1C (https://drive.google.com/open?id=1_67Lwh4ATjaUkKTpdhqNA2vhhSxMhfoh) | V2 | YES | x | x | x | x | original
1D (https://drive.google.com/open?id=1RDZathABUe1AxNllos18oBRUGkUw-BAb) | V2 | YES | x | x |  | x | x
1E (https://drive.google.com/open?id=1B7jEgQfvgjZIKbfW8eR9qm2PDLYRcFFX) | V2 | YES | x | x | x | x | original
1F (https://drive.google.com/open?id=1y8psJsldf8GOPKXdI3_7jAN-0VefmuVb) | V1 | YES | x | x | x | x | -
1G (https://drive.google.com/open?id=1Ak0bagtonjeBe0T45ml7mh9V5vKH_FoI) | V2 | YES | x | x | x | x | original
1H (https://drive.google.com/open?id=15tp_vGgbK5-4zzthz0W8wuq2zgKokja6) | V2 | YES | x | x | x | x | original
1J (https://drive.google.com/open?id=1EMft8Du0dvrSSlstsShqV16Nnrlb4EO_) | V2 | - | x | x |  | x | x
1K (https://drive.google.com/open?id=1B-AwkTkUdHQS0dThuP6mM5L_0XIFZ2QS) | V2 | YES | x | x | x | x | original
2A (https://drive.google.com/open?id=1XILFfrJerwAeHeN4xKdQH-99VN9y0QS7) | V2 | YES | x | x | x | x | original
2B (https://drive.google.com/open?id=1i7lErxBcw13LxRubiAB_0upxTGrTLBvi) | V2 | YES | x | x | x | x | original
2C (https://drive.google.com/open?id=1HmSkhlRiy_w_xIcPrlD-Gu21Q1sHCajk) | V2 | YES | x | x | x | x | original
2D (https://drive.google.com/open?id=1ih9AM9nSu6WpURV8EnXu6Q1HkOh5dSXM) | V2 | YES | x | x |  | x | x
2E (https://drive.google.com/open?id=1ilbwUzFLn2Zr9CQ_v673T9KjSALf_GzB) | V2 | YES | x | x | x | x | original
2F (https://drive.google.com/open?id=1H2B7fJmOymk8ZeyITqVgqJIR9EbewGjs) | V2 | YES | x | x |  | x | x
2G (https://drive.google.com/open?id=1GXDi1coA9HtIo5F2GTLcPhpAh_IiHrmJ) | V2 | - | x | x |  | x | x
2H (https://drive.google.com/open?id=18itspidwzvb4KFHkqj1122TxuhHxILwX) | V2 | YES | x | x | x | x | original
2J (https://drive.google.com/open?id=12YgGEJrua5a-agu15lV4vezflw1cOjQ4) | V2 | YES | x | x | x | x | original
2K (https://drive.google.com/open?id=1mdMrKj4CCNPy7BlChSDOU2hQAJONhZzU) | V2 | YES | x | x | x | x | original
2L (https://drive.google.com/open?id=14mzIl-szkFL_WWXlsFZ9T_x3Mt5RAOn0) | V2 | YES | x | x | x | x | original
2M (https://drive.google.com/open?id=1-X_VRvOqUUm_bcQ792NJw8TTxR5Kl3lr) | V2 | YES | x | x | x | x | original
3C (https://drive.google.com/open?id=1ofYuI7zJYOx0Em5kOgymDe9L2TWaIZ-_) | V2 | - | x | x | x | x | original
3D (https://drive.google.com/open?id=1X9eTLHcdh-lSX2OXG4OLDNwPRG5eoz9l) | V2 | YES | x | x | x | x | original
3E (https://drive.google.com/open?id=1m_ACLfEw9sFFcCd16wQnkI9wa3WI7gK9) | V2 | - | x | x |  | x | x
3F (https://drive.google.com/open?id=1CIBdXiHhWBrM6LwlY-yGooPill1DRTQ7) | - | -
3G (https://drive.google.com/open?id=1c2xmouFbs4cNAvpeHuAdgNreh8kFEC2V) | - | - |  |  |  |  | x
3H (https://drive.google.com/open?id=1t7wkFvS4sGjdMU60zYacdFSrl4pYayl_) | - | - |  |  |  |  | x
3J (https://drive.google.com/open?id=1N0-R1KTkpoZjXWmN7r0U_myR9XBY5SDj) | V2 | - | x | x |  | x | x
3L (https://drive.google.com/open?id=13pmWKIsTMFsSuBTJ-HZb5DVIowIXTS_s) | V2 | YES | x | x | x | x | original
4E (https://drive.google.com/open?id=16nGNQgv2r19h9agxYjXmQ8rC4v330dYf) | V2 | YES | x | x | x | x | original
4F (https://drive.google.com/open?id=1bmJc7h6PrfobWHjtATEPhVDZqxi3ORaa) | V2 | - | x | x |  | x | x
4G (https://drive.google.com/open?id=1nHAP6VZOPX4PWClDeQpEHh4MuzIQchEa) | V1 | YES | x | x | x | x | -
4H (https://drive.google.com/open?id=1a78u8iOyRFbuJtQlj9X51FknS9EfCDih) | V2 | - | x | x |  | x | x
4J (https://drive.google.com/open?id=1zZjefBVzFC9BP-YmMKfQZMWa1XGkqomj) | V2 | YES | x | x | x | x | original
4K (https://drive.google.com/open?id=1qWFlabv0TeVOBvOIJQuvHlR1H3AMOPvN) | V2 | - | x | x |  | x | x
4L (https://drive.google.com/open?id=176NV2NM9yvfuW1EMU3iBS768FxgmXjUS) | V2 | - | x | x |  | x | x
5B (https://drive.google.com/open?id=1cC0P-G66cPSNnf6v6z8opZCNyporo74Y) | V2 | YES | x | x | x | x | original
5C (https://drive.google.com/open?id=1q_N74b1OZrCze7zuXy5fm0ASU07tWzh3) | V1 | YES | x | x | x | x | -
5E (https://drive.google.com/open?id=1aKSCelAY002Ihje9mdJi7jFh0OB4j8XZ) | V2 | YES | x | x |  | x | x
5G (https://drive.google.com/open?id=1ghdX_COwJq4oYlhj-qYPypK_2GlrWyQZ) | V2 | - | x | x |  | x | x
5H (https://drive.google.com/open?id=1MR24L4GDI5x861k8SMrgm71xRfm55Hiv) | V2 | - | x | x |  | x | x

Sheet: LNAs
LNAs outside of feeds
Feed Lab | sn0085A | broken MMIC (crack)
Feed Lab | sn0061A | broken wirebond |  | Handed to Alex Leder UCB for wire bond repair 09/2022
PY-024 | sn0030A |  | OK
PY-024 | sn0068A |  | OK
PY-009 | sn0021A | run wet, 6 month with ice | OK
PY-009 | sn0019A | run wet, 6 month with ice | OK
Feed Lab | sn0013A | single LNA previous paired with sn0061A | OK
Feed Lab | sn0028A | from 2a broken LNA X pol
Minex | sn0041A | from 2a broken LNA X pol
PY-023 | sn0001A | IAF LNAs | OK
PY-023 | sn0004A | IAF LNAs | OK
PY-025 | sn0003A | lnf LNAs | OK
PY-025 | sn0002A | lnf LNAs | OK

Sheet: PAX Boxes
PAX Box Number | Original Feed | Feed information source | Current Location | Status | Comments
PB-001 | 1B | Pulled out and recorded & feed parts spreadsheet | Lab 1 | Calibrated | A little bit of bumpiness in both passbands
PB-002 | 3D | Feed parts spreadsheet | Missing (possibly at Minex)
PB-003 | 2C | Pulled out and recorded & feed parts spreadsheet | Lab 1 | Needs testing | Y passband not ideal
PB-004 | 5H | Feed parts spreadsheet | Lab 1 | Calibrated
PB-005 | 2B | Feed parts spreadsheet | 2B | Calibrated and inside working feed
PB-006 | 2H | Feed parts spreadsheet | 2H | Calibrated and inside working feed
PB-007 | Unknown | Not listed in feed parts spreadsheet | Workshop | Missing a control board | Not in working condition
PB-008 | 3L | Feed parts spreadsheet | Lab 1 | Calibrated
PB-009 | 3C | Feed parts spreadsheet | Workshop | Calibrated | Passbands are a bit bumpy
PB-010 | Unknown | Not listed in feed parts spreadsheet | Lab 1 | Calibrated | Control board was replaced with PAX 17’s & passbands are bumpy
PB-011 | 2J | Feed parts spreadsheet | Lab 1 | Calibrated (maybe needs fixing) | Issue with X-Pol fiber or board causing X passband to be ugly
PB-012 | 1A | Feed parts spreadsheet | Missing (possibly at Minex) | Calibrated (it was calibrated in February according to measurement file)
PB-013 | 2A | Feed parts spreadsheet | 2A | Calibrated and inside working feed | Y detectors saturate at 1.7dBm on noise measurement & has a bumpy passband
PB-014 | 2K | Pulled out and recorded & feed parts spreadsheet | Lab 1 | Calibrated
PB-015 | Unknown | Not listed in feed parts spreadsheet | Lab 1 | Calibrated | Bumpy X passband
PB-016 | 5E | Feed parts spreadsheet | Lab 2 | Calibrated | X saturates at 1.7dbm for both x measurements. Bumpy passbands
PB-017 | 4J | Feed parts spreadsheet & piece of tape on box | Workshop | Missing a control board | Not in working condition
PB-018 | Unknown | Not listed in feed parts spreadsheet | Unknown if it actually exists
PB-019 | 5G | Feed parts spreadsheet | Lab 1 | Calibrated | X saturates at 1.7dbm for both x measurements. Bumpy passbands
PB-020 | Unknown | Not listed in feed parts spreadsheet | Lab 2
PB-021 | 2F | Pulled out and recorded & feed parts spreadsheet | Workshop | Missing both PAMs | Not in working condition
PB-022 | 1F | Feed parts spreadsheet | 1F | Calibrated and inside working feed | Detectors saturate at 1.8dBm for both x&y on noise measurements
PB-023 | Unknown | Not listed in feed parts spreadsheet | Unknown if it actually exists
PB-024 | 1D | Pulled out and recorded & feed parts spreadsheet | Lab 1 | Calibrated | Y detector saturate at 1.5dBm on noise measurement & bumpy passbands
PB-025 | Unknown | Not listed in feed parts spreadsheet | Lab 1 | Calibrated (maybe needs fixing) | Low X gain (maybe broken amplifier)
PB-026 | 1K | Feed parts spreadsheet | 1K | Calibrated and inside working feed
PB-027 | 3J | Pulled out and recorded & feed parts spreadsheet | Workshop | Calibrated (maybe needs fixing) | Bowl shaped Y passband so filter or slope supporter possibly broken
PB-028 | Unknown | Not listed in feed parts spreadsheet | Lab 1 | Calibrated (maybe needs fixing) | Y saturates at 1dBm on noise measurement & bowl shape passbands (broken filter or slope supporter maybe)
PB-029 | 2E | Feed parts spreadsheet | Lab 1 | Calibrated | Y passband and power sweep are both unusual
PB-030 | Unknown | Not listed in feed parts spreadsheet | Lab 1 | Calibrated | X passband is 10dBm less than Y’s
PB-031 | 5C | Feed parts spreadsheet | 5C | Calibrated and inside working feed | Low Gain on X-Pol, looks like fiber link
PB-032 | 2G | Pulled out and recorded & feed parts spreadsheet | Workshop | Missing both PAMs | Y passband indicates there is filter or slope supporter broken
PB-033 | 4L | Pulled out and recorded & feed parts spreadsheet | Lab 1 | Calibrated
PB-034 | 1G | Feed parts spreadsheet | Lab 1 | Calibrated | Bumpy X passband
PB-035 | 3E | Pulled out and recorded & feed parts spreadsheet | Lab 1 | Calibrated | Bumpy and sloping X passband
PB-036 | Unknown | Not listed in feed parts spreadsheet | Workshop | Needs testing
PB-037 | 4G | Feed parts spreadsheet | 4G | Calibrated and inside working feed | Dip in passband of X-Pol
PB-038 | Unknown | Not listed in feed parts spreadsheet | Lab 1 | Calibrated | Control board replaced with PAX 7’s & bumpy Y passband
PB-039 | 1H | Feed parts spreadsheet | Lab 1 | Calibrated
PB-040 | 1C | Feed parts spreadsheet | 1C | Calibrated and inside working feed | Possible problem with temp stabilization & bumpy passbands
PB-041 | 2D | Pulled out and recorded & feed parts spreadsheet | Workshop | Missing both PAMs | Not in working condition
PB-042 | 4K | Pulled out and recorded & feed parts spreadsheet | Lab 1 | Calibrated
PB-043 | Unknown | Not listed in feed parts spreadsheet | Lab 1 | Calibrated
PB-044 | 2L | Pulled out and recorded & feed parts spreadsheet | Lab 1 | Calibrated | Bumpy passbands
PB-045 | 5B | Feed parts spreadsheet | Lab 1 | Calibrated | Bumpy X passband

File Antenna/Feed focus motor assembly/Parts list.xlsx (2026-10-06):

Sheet: all parts
 |  |  |  |  | Feed focus motor assembly
 |  |  |  |  | 2026-10-02
Description | Purpose | Notes | Order link | Qty per assembly | Manufacturer | Mfg part # | Supplier | Supplier part # | Order qty | Price ea | Total cost
AC synchronous motor, 120Vac supply voltage, 0.47A rated current, 72rpm, 60Hz, NEMA 34 | Motor | Same product may be branded Kollmorgen or Pacific Scientific. No longer made. Some available through Wake Automation. Found some available on eBay. | https://www.ebay.com/itm/276829447492; https://www.ebay.com/itm/277300786756 (https://shop.iautomation.com/products/SN32HRYY-LNK-NS-00) | 1 | Pacific Scientific/Kollmorgen | SN32HRYY-LNK-NS-00 | Wake Industrial, eBay | SN32HRYY-LNK-NS-00 | 1 | $590.00
Magnetic read contact | Read contact |  | https://www.mouser.com/en/ProductDetail/Littelfuse/59065-010?qs=moDRE%2FDosU2XYkzd%2FiBrBg%3D%3D | 2 | Littelfuse | 59065-010 | Mouser | 934-59065-010 | 1 | $4.88
Wirewound resistor - chassis mount 50watt 200ohm 1% | Resistor |  | https://www.mouser.com/en/ProductDetail/Vishay-Dale/RH050200R0FE02?qs=%252B%2F1MMOhkBTcGlLwZUqit8Q%3D%3D | 1 | Vishay/Dale | RH050200R0FE02 | Mouser | 71-RH050200R0FE02 | 1 | $14.82
10.0 MFD motor run capacitor, 370Vac, 50-60Hz, oval can (wd 2", dp 1.25") | Capacitor |  | https://www.northamericahvac.com/oem-amrad-run-capacitor-10-10-0-uf-mfd-370-440-volt-va2000-37-106-made-in-usa/ | 1 | Amrad Engineering | USA2035 | North America HVAC | n/a | 1 | $15.65
8-32 3/8" button head screws | Secure cable clamp, secure standoffs and cover |  | https://www.mcmaster.com/products/screws/rounded-head-screws-2~/length~3-8-1/thread-size~8-32/drive-style~phillips/ | 5 | McMaster-Carr | 91772A192 | McMaster-Carr | 91772A192 | 100 | $0.099
8-32 1.5" round female standoffs | Spacer between cover and plate |  | https://www.mcmaster.com/93330A482/ | 2 | McMaster-Carr | 93330A482 | McMaster-Carr | 93330A482 | 1 | $0.76
Narrow 1/4" 8-32 hex nuts | Secure cable clamp |  | https://www.mcmaster.com/90730A009/ | 1 | McMaster-Carr | 90730A009 | McMaster-Carr | 90730A009 | 100 | $0.0798
10-32 1/2" socket head screws | Secure read contact flat bracket | Already have some on hand | https://www.mcmaster.com/92196A269/ | 1 | McMaster-Carr | 92196A269 | McMaster-Carr | 92196A269 | 100 | $0.1465
10-32 5/8" socket head screws | Secure motor to plate | Can reuse from retrofitted motors | https://www.mcmaster.com/92196A271/ | 4 | McMaster-Carr | 92196A271 | McMaster-Carr | 92196A271 | 100 | $0.1533
10-32 1.25" partially threaded socket head screws | Secure read contact long bracket |  | https://www.mcmaster.com/92196A276/ | 1 | McMaster-Carr | 92196A276 | McMaster-Carr | 92196A276 | 50 | $0.28
6-32 5/16" button head screws | Secure capacitor flanges to plate |  | https://www.mcmaster.com/91772A145/ | 2 | McMaster-Carr | 91772A145 | McMaster-Carr | 91772A145 | 100 | $0.062
4-40 1/4" button head screws | Secure resistor to plate |  | https://www.mcmaster.com/91772A106/ | 2 | McMaster-Carr | 91772A106 | McMaster-Carr | 91772A106 | 100 | $0.0488
Cable clamp | Secure read contact cable to plate |  | https://www.mcmaster.com/8876T13/ | 1 | McMaster-Carr | 8876T13 | McMaster-Carr | 8876T13 | 100 | $0.1219
Rubber grommet, 7/16" OD | Protect motor cable |  | https://www.mcmaster.com/9307K11/ | 1 | McMaster-Carr | 9307K11 | McMaster-Carr | 9307K11 | 50 | $0.1162
7-wire, double-shielded control cable, 20AWG, 5ft | Control cable |  | https://www.mcmaster.com/6650T29-6650T291/ | 1 | Alpha Wire | 79205 | McMaster-Carr | 6650T29 | 1 | $20.5500
12-position terminal block | Wiring |  | https://www.mouser.com/en/ProductDetail/Altech/40.112?qs=DeBbiv%2F5BpB0AUS9j8M0Aw%3D%3D | 1 | Altech | 40.112 | Mouser | 845-40.112 | 50 | $0.0980
7-pin circular DIN connector | Plug into rimbox |  | https://www.mouser.com/en/ProductDetail/Amphenol-Tuchel/T3475-551?qs=dGKrImpajHo7pbFrxtfPgw%3D%3D | 1 | Amphenol Tuchel | T3475-551 | Mouser | 523-T3475551 | 1 | $12.0500
Smaller cable clamp | Cable clamp - control cable to plate | Might have some on-hand
Larger cable clamp | Cable clamp - read contact to plate | Might have some on-hand
Read contact flat bracket | Hold read contact to antenna | Custom
Read contact post bracket | Hold read contact to plate (inside cover) | Custom
Metal half clamp | Capacitor flanges, secure cap to plate | Cannot find exact size, is it custom? Might have some on-hand
Cover | Custom sheet metal to cover electronics
Plate | Custom sheet metal to hold electronics
Timing belt pulley, 5M pitch, 9mm belt, 25 teeth, keyed shaft | Couple motor to belt | Cannot find for sale for the life of me. Is it custom-built?
Ferrules, 20AWG | Secure connections to terminal | Assume on-hand
Eye crimps, 20AWG | Ground wires | Assume on-hand

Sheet: spares order
Spare assembly and retrofitting, October 2026 |  |  |  |  | Order cost: | 2423.48
Part | Manufacturer | Mfg. part # | Qty | Cost ea. | Total cost | Order link
AC synchronous motor | Pacific Scientific/Kollmorgen | SN32HRYY-LNK-NS-00 | 4 | 489 | 1956 | See attached quote
Read contact | Littelfuse | 59065-010 | 20 | 4.88 | 97.6 | https://www.mouser.com/en/ProductDetail/Littelfuse/59065-010?qs=moDRE%2FDosU2XYkzd%2FiBrBg%3D%3D
Wirewound resistor | Vishay/Dale | RH050200R0FE02 | 5 | 14.82 | 74.1 | https://www.mouser.com/en/ProductDetail/Vishay-Dale/RH050200R0FE02?qs=%252B%2F1MMOhkBTcGlLwZUqit8Q%3D%3D
Motor run capacitor | Amrad Engineering | USA2035 | 5 | 15.65 | 78.25 | https://www.northamericahvac.com/oem-amrad-run-capacitor-10-10-0-uf-mfd-370-440-volt-va2000-37-106-made-in-usa/
8-32 3/8" button head screws | McMaster-Carr | 91772A192 | 100 | 0.0990 | 9.9 | https://www.mcmaster.com/products/screws/rounded-head-screws-2~/length~3-8-1/thread-size~8-32/drive-style~phillips/
10-32 1/2" socket head screws | McMaster-Carr | 92196A269 | 100 | 0.1465 | 14.65 | https://www.mcmaster.com/92196A269/
10-32 1.25" partially threaded socket head screws | McMaster-Carr | 92196A276 | 50 | 0.28 | 14 | https://www.mcmaster.com/92196A276/
6-32 5/16" button head screws | McMaster-Carr | 91772A145 | 100 | 0.062 | 6.2 | https://www.mcmaster.com/91772A145/
4-40 1/4" button head screws | McMaster-Carr | 91772A106 | 100 | 0.0488 | 4.88 | https://www.mcmaster.com/91772A106/
7-wire, double-shielded control cable, 20AWG, 5ft | Alpha Wire | 79205 | 5 | 20.550 | 102.75 | https://www.mcmaster.com/6650T29-6650T291/
7-pin circular DIN connector | Amphenol Tuchel | T3475-551 | 5 | 12.05 | 60.25 | https://www.mouser.com/en/ProductDetail/Amphenol-Tuchel/T3475-551?qs=dGKrImpajHo7pbFrxtfPgw%3D%3D
12-position terminal block | Altech | 40.112 | 50 | 0.098 | 4.9 | https://www.mouser.com/en/ProductDetail/Altech/40.112?qs=DeBbiv%2F5BpB0AUS9j8M0Aw%3D%3D

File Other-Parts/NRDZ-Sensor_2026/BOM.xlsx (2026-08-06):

Price | Quantity | Unit | Description | Manufacturer | Manu. Part No. | Distributor | Link | Datasheet | Distributor Part No.
3.06 | 1 | Pack of 100 | M3 Zinc-Plated Steel Hex Nut | McMaster-Carr | 90591A250 | McMaster-Carr | ↗ (https://www.mcmaster.com/90591A250/) | - | 90591A250
6.38 | 1 | Pack of 100 | 6-32 Zinc-Plated Steel Locknut | McMaster-Carr | 90675A007 | McMaster-Carr | ↗ (https://www.mcmaster.com/90675A007/) | - | 90675A007
5.35 | 1 | Pack of 100 | 8-32 Zinc-Plated Steel Locknut | McMaster-Carr | 90675A009 | McMaster-Carr | ↗ (https://www.mcmaster.com/90675A009/) | - | 90675A009
1.43 | 2 | Each | 6-32 1/2" Male-Female Hex Standoff | McMaster-Carr | 91075A442 | McMaster-Carr | ↗ (https://www.mcmaster.com/91075A442/) | - | 91075A442
1.85 | 2 | Each | 6-32 1 1/2" Male-Female Hex Standoff | McMaster-Carr | 91075A448 | McMaster-Carr | ↗ (https://www.mcmaster.com/91075A448/) | - | 91075A448
4.81 | 1 | Pack of 100 | M3 Stainless Steel Oversized Washer | McMaster-Carr | 91116A120 | McMaster-Carr | ↗ (https://www.mcmaster.com/91116A120/) | - | 91116A120
12.71 | 1 | Pack of 100 | M3 6mm Steel Pan Head Slotted Screw | McMaster-Carr | 91200A112 | McMaster-Carr | ↗ (https://www.mcmaster.com/91200A112/) | - | 91200A112
15.93 | 1 | Pack of 50 | M2.5 5mm Socket Head Screw | McMaster-Carr | 91290A100 | McMaster-Carr | ↗ (https://www.mcmaster.com/91290A100/) | - | 91290A100
9.43 | 1 | Pack of 50 | 8-32 3/8" Phillips Rounded Head Screw | McMaster-Carr | 91400A192 | McMaster-Carr | ↗ (https://www.mcmaster.com/91400A192/) | - | 91400A192
6.72 | 1 | Pack of 50 | M3 45mm Phillips Flat Head Screw | McMaster-Carr | 91420A138 | McMaster-Carr | ↗ (https://www.mcmaster.com/91420A138/) | - | 91420A138
4.46 | 1 | Pack of 100 | No.8 Internal Tooth Lock Washer | McMaster-Carr | 91757A105 | McMaster-Carr | ↗ (https://www.mcmaster.com/91757A105/) | - | 91757A105
11.8 | 1 | Pack of 100 | M2.5 20mm Button Head Hex Screw | McMaster-Carr | 92095A115 | McMaster-Carr | ↗ (https://www.mcmaster.com/92095A115/) | - | 92095A115
3.07 | 1 | Pack of 100 | No.6 Steel Washer | McMaster-Carr | 92141A008 | McMaster-Carr | ↗ (https://www.mcmaster.com/92141A008/) | - | 92141A008
2.89 | 1 | Pack of 100 | M2.5 Steel Washer | McMaster-Carr | 93475A196 | McMaster-Carr | ↗ (https://www.mcmaster.com/93475A196/) | - | 93475A196
1.34 | 25 | Each | 8-32 1/2" Male-Female Hex Standoff | McMaster-Carr | 93620A452 | McMaster-Carr | ↗ (https://www.mcmaster.com/93620A452/) | - | 93620A452
2.3 | 4 | Each | M2.5 10mm Male-Female Hex Standoff | McMaster-Carr | 93655A096 | McMaster-Carr | ↗ (https://www.mcmaster.com/93655A096/) | - | 93655A096
19.32 | 1 | Pack of 100 | 6-32 3/4" Steel Threaded Rod | McMaster-Carr | 95475A222 | McMaster-Carr | ↗ (https://www.mcmaster.com/95475A222/) | - | 95475A222
2.57 | 4 | Each | M3 45mm Male-Female Hex Standoff | McMaster-Carr | 98952A402 | McMaster-Carr | ↗ (https://www.mcmaster.com/98952A402/) | - | 98952A402
2.52 | 2 | Each | M3 30mm Male-Female Hex Standoff | McMaster-Carr | 98952A407 | McMaster-Carr | ↗ (https://www.mcmaster.com/98952A407/) | - | 98952A407
12.2 | 1 | Each | Power Supply 5V 7A Chassis Mount | MEAN WELL | LRS-35-5 | Mouser | ↗ (https://www.mouser.com/en/ProductDetail/MEAN-WELL/LRS-35-5?qs=vDxCgdWo2h86Om%2Far%2FQvsg%3D%3D) | ↗ (https://www.meanwellusa.com/webapp/product/search.aspx?prod=LRS-35) | 709-LRS35-5
13.42 | 1 | Each | Power Supply 12V 4.2A Chassis Mount | MEAN WELL | LRS-50-12 | Mouser | ↗ (https://www.mouser.com/en/ProductDetail/MEAN-WELL/LRS-50-12?qs=vDxCgdWo2h8cZVniPTDIfQ%3D%3D) | ↗ (https://www.mouser.com/datasheet/3/67/1/LRS_50_SPEC.PDF) | 709-LRS50-12
122.15 | 1 | Each | Linear Power Supply 12V 1.7A | Bel Power Solutions | HB12-1.7-AG | Mouser | ↗ (https://www.mouser.com/en/ProductDetail/Bel-Power-Solutions/HB12-1.7-AG?qs=UrIO86DvchfftFtWbOQckQ%3D%3D) | ↗ (https://www.belfuse.com/media/datasheets/products/power-supplies/ds-bps-linear-series.pdf) | 784-HB12-1.7-AG
379.9 | 1 | Each | Jetson Orin Nano | Nvidia | P3766 | Nvidia | ↗ (https://www.nvidia.com/en-us/autonomous-machines/embedded-systems/jetson-orin/nano-super-developer-kit/) | ↗ (https://nvdam.widen.net/s/zkfqjmtds2/jetson-orin-datasheet-nano-developer-kit-3575392-r2) | P3766
1735 | 1 | Each | USRP B200mini | Ettus | 785887-01 | Ettus | ↗ (https://www.ettus.com/wp-content/uploads/2019/01/USRP_B200mini_Data_Sheet-1.pdf) | ↗ (https://www.mcmaster.com/90591A250/) | 785887-01
5.06 | 1 | Each | Power Distribution Block, Red | Phoenix Contact | 3273158 | Mouser | ↗ (https://www.mouser.com/en/ProductDetail/Phoenix-Contact/3273158?qs=gt1LBUVyoHkzQ5vffThASw%3D%3D) | ↗ (https://www.mouser.com/datasheet/3/507/10/phoenix_contact_3273158_en.pdf) | 651-3273158
5.06 | 1 | Each | Power Distribution Block, Black | Phoenix Contact | 3273168 | Mouser | ↗ (https://www.mouser.com/en/ProductDetail/Phoenix-Contact/3273168) | ↗ (https://www.mouser.com/datasheet/3/507/7/phoenix_contact_3273168_en.pdf) | 651-3273168
135.4 | 1 | Each | Amplifier (14.3dB, 500kHz-5GHz) | Mini-Circuits | ZX60-43-S+ | Mouser | ↗ (https://www.mouser.com/en/ProductDetail/Mini-Circuits/ZX60-43-S%2b?qs=xZ%2FP%252Ba9zWqbaGStvh6mpuA%3D%3D) | ↗ (https://www.mouser.com/datasheet/3/3705/1/ZX60-43-S+.pdf) | 139-ZX60-43-S
178.45 | 1 | Each | Bias-Tee | Mini-Circuits | ZX85-12G-S+ | Mouser | ↗ (https://www.mouser.com/en/ProductDetail/Mini-Circuits/ZX85-12G-S%2b?qs=CiayqK2gdcITcMx0C1pwnw%3D%3D) | ↗ (https://www.mouser.com/datasheet/3/3705/1/ZX85-12G-S+.pdf) | 139-ZX85-12G-S+
- | 1 | Each | White Rabbit Lite Embedded Node | Safran | WR-LEN | Safran | ↗ (https://safran-navigation-timing.com/product/white-rabbit-len/) | ↗ (https://safran-navigation-timing.com/wp-content/uploads/2023/07/SAFRAN_White-Rabbit-LEN_Datasheet_6-5-2023_US.pdf) | WR-LEN
 | 1 | Each | Plate-0, Base Plate | Front Panel Express | - | Front Panel Express
 | 1 | Each | Plate-1, Top Layer Plate | Front Panel Express | - | Front Panel Express
 | 1 | Each | FrontPlate | Front Panel Express | - | Front Panel Express
31.35 | 2 | Each | EMI Fan Vent | TE Connectivity | Kemvent40 | Mouser | ↗ (https://www.mouser.com/en/ProductDetail/TE-Connectivity-Raychem/Kemvent40?qs=rQFj71Wb1eUKiLCfYWpB9g%3D%3D) | ↗ (https://www.te.com/commerce/DocumentDelivery/DDEController?Action=showdoc) | 571-KEMVENT40
16.54 | 1 | Each | Axial Fan | Sunon Fans | PF40281B2-1000U-A9H | DigiKey | ↗ (https://www.digikey.com/en/products/detail/sunon-fans/PF40281B2-1000U-A9H/15996436) | ↗ (https://www.sunonusa.com/wp-content/uploads/2026/05/PF40281B2-1000U-A9H-D04165230G-00-0.pdf) | 259-PF40281B2-1000U-A9H
22.14 | 1 | Each | Axial Fan 5.52W 12VDC | Sunon Fans | GF40282B1-1000U-ADP | DigiKey | ↗ (https://www.digikey.com/en/products/detail/sunon-fans/gf40282b1-1000u-adp/22611498) | ↗ (https://www.sunonusa.com/wp-content/uploads/2026/01/GF40282B1-1000U-ADP-D04176790G-01-0_Ref.pdf) | 259-GF40282B1-1000U-ADP
159.75 | 1 | Each | SMA Feedthrough | Pasternack | PE9184 | Mouser | ↗ (https://www.mouser.com/en/ProductDetail/Pasternack/PE9184?qs=3GbUB62Nf7eVzObJCzhp2Q%3D%3D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) | ↗ (https://www.pasternack.com/images/productpdf/PE9184.pdf) | 28-PE9184
6.91 | 1 | Each | Fiber FC Feedthrough | L-Com | FOA-FCAM1-MC0D-SMH | Mouser | ↗ (https://www.mouser.com/en/ProductDetail/L-Com/FOA-FCAM1-MC0D-SMH?qs=%252BHhoWzUJg4LXAD16N8KjIw%3D%3D) | ↗ (https://www.l-com.com/Images/Downloadables/2D/FOA-FCAM1-MC0D-SMH_2D.PDF) | 17-FOAFCAM1MC0DSMH

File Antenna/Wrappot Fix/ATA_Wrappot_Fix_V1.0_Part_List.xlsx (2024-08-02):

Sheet: Tabelle2
Quantity | Unit | Designation | Manufacturer | Manufacturer Part number | Distributor | Distributor Part Number
1 |  | RF-Switch | AP
1 | Each | PCB V1.0 | AP | ATA_Wrappot_Fix_V1.0.zip
1 | Each | Thick Film Resistors - SMD 0805 1.24K | Panasonic | ERJ-PB6B1241V | Mouser | 667-ERJ-PB6B1241V
2 | Each | Thin Film Resistors - SMD 0805 910 | Panasonic | ERA-6APB911V | Mouser | 667-ERA-6APB911V
1 | Each | Thick Film Resistors - SMD 0805 698 | Panasonic | ERJ-PB6B6980V | Mouser | 667-ERJ-PB6B6980V
1 | Each | Thin Film Resistors - SMD 0805 732 | TE Connectivity | RN73C2A732RBTDF | Mouser | 279-RN73CA-732
1 | Each | Thin Film Resistors - SMD 0805 91K | Panasonic | ERA-6ARB913V | Mouser | 667-ERA-6ARB913V
1 | Each | Tantalum Capacitors - Polymer 25V 1uF | KYOCERA AVX | TCJP105M025R0500E | Mouser | 581-TCJP105M025R500E
2 | Each | Multilayer Ceramic Capacitors MLCC - SMD/SMT 50V .1uF | KYOCERA AVX | KAM21BR71H104JT | Mouser | 581-KAM21BR71H104JT
1 | Each | Tantalum Capacitors - Solid SMD 10uF 25volt 10% B Case | Vishay | 293D106X9025B2TE3 | Mouser | 74-293D106X9025B2TE3
1 | Each | Power Inductors - SMD 10uH 960mohms 464mA 10% | Delevan | SP1210R-103K | Mouser | 807-SP1210R-103K
1 | Each | Voltage References | Texas Instruments | LM4140CCM-2.5/NOPB | Mouser | 926-LM4140CCM2.5NOPB
1 | Each | Operational Amplifiers - Op Amps Quad | Analog Devices | LT1359CS#PBF | Mouser | 584-LT1359CS#PBF
1 | Each | Headers & Wire Housings RECEPTACLE 3 POS | Molex | 43645-0300 | Mouser | 538-43645-0300
1 | Each | Headers & Wire Housings R/A HEADER 3 POS TIN SINGLE ROW | Molex | 43650-0300 | Mouser | 538-43650-0300
3 | Each | Terminals FEMALE TERM 20-24 | Molex | 43030-0009 | Mouser | 538-43030-0009
1 | Each | Hook-up Wire 20AWG 10/30 MPPE 100ft SPOOL BLACK | Alpha Wire | 6714 BK005 | Mouser | 602-6714-100-02
1 | Each | Hook-up Wire 20AWG 10/30 MPPE 100ft SPOOL RED | Alpha Wire | 6714 RD005 | Mouser | 602-6714-100-03
1 | Each | Hook-up Wire 20AWG 10/30 MPPE 100FT SPOOL YELLOW | Alpha Wire | 6714 YL005 | Mouser | 602-6714-100-05
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

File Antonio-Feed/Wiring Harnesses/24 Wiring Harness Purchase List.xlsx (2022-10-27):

 | Material | Manufacturer | Order Number of Manufaturer | Distributor | Order Number of Distributor | Amount | Price
WIRE | Orange 14 awg | ALPHA WIRE | 6717 OR005 | Mouser | 602-6717-100-08 | 1 | $151.29
 | White 14 awg | ALPHA WIRE | 6717 WH005 | Mouser | 602-6717-100-01 | 1 | $149.56
 | Red 14 awg | ALPHA WIRE | 6717 RD005 | Mouser | 602-6717-100-03 | 2 | $299.12
 | Black 14 awg | ALPHA WIRE | 6717 BK005 | Mouser | 602-6717-100-02 | 2 | $297.38
 | Black 20 awg | ALPHA WIRE | 6714 BK005 | Mouser | 602-6714-100-02 | 2 | $112.76
 | Blue 20 awg | ALPHA WIRE | 6714 BL005 | Mouser | 602-6714-100-06 | 2 | $116.00
 | Red 20 awg | ALPHA WIRE | 6714 RD005 | Mouser | 602-6714-100-03 | 3 | $170.10
 | Orange 24 awg | ALPHA WIRE | 6712 OR005 | Mouser | 602-6712-100-08 | 1 | $42.00
 | Yellow 24 awg | ALPHA WIRE | 6712 YL005 | Mouser | 602-6712-100-05 | 1 | $42.23
 | Black 24 awg | ALPHA WIRE | 6712 BK001 | Mouser | 602-6712-1000-02 | 1 | $202.62
 | Violet 28 awg | ALPHA WIRE | 6710 VI001 | Mouser | 602-6710-1000-10 | 1 | $184.76
 | Brown 28 awg | ALPHA WIRE | 6710 BR001 | Mouser | 602-6710-1000-07 | 1 | $184.76
 | Orange 28 awg | ALPHA WIRE | 6710 OR001 | Mouser | 602-6710-1000-08 | 0
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

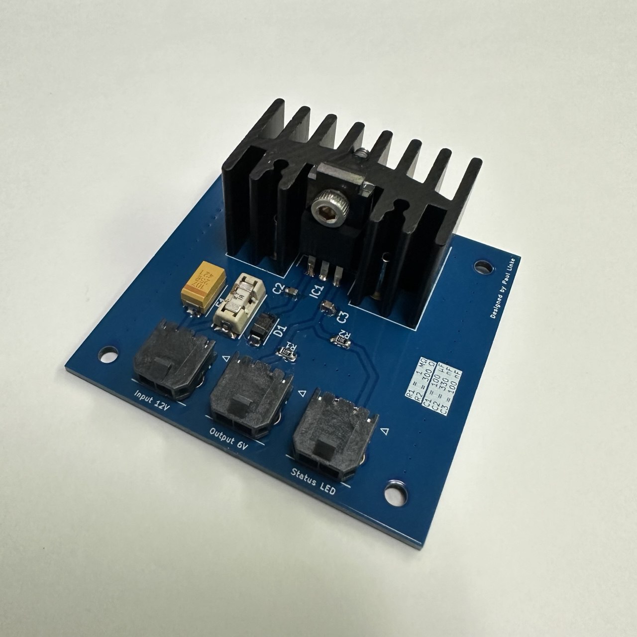
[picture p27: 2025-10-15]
Analog-Signal-Components/RFoF/Linear_Voltage_Regulator_6V/Images/Linear_Voltage_Regulator_real.png

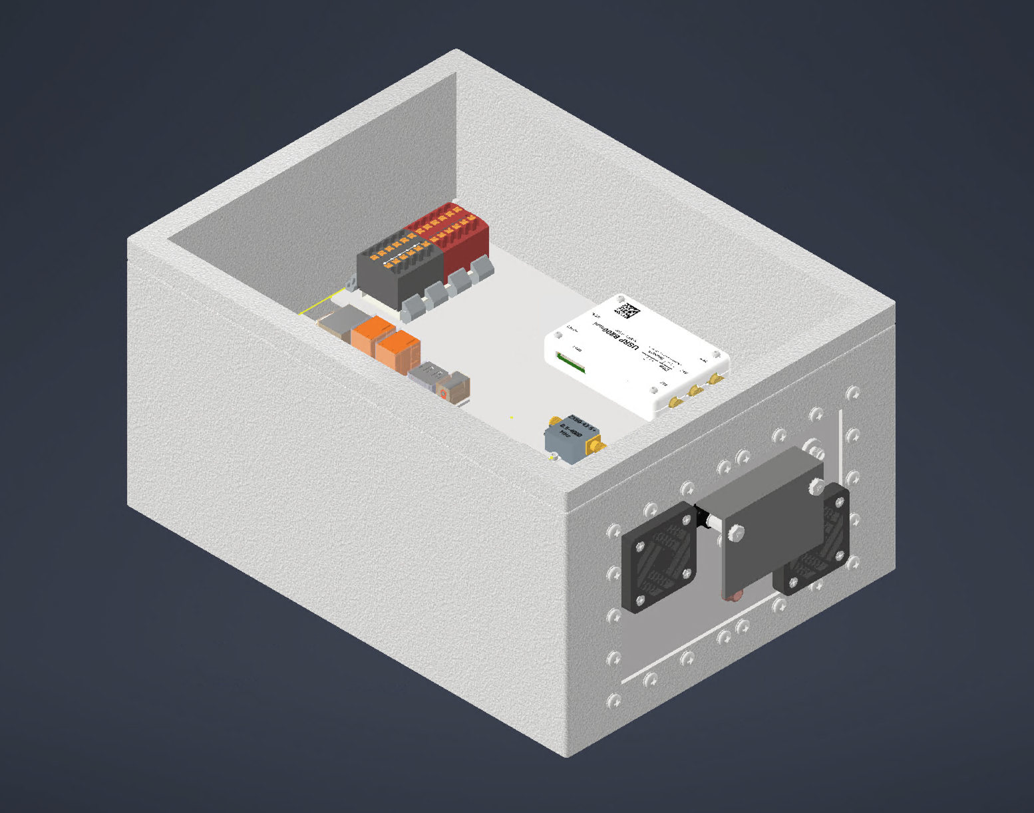
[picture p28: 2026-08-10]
Other-Parts/NRDZ-Sensor_2026/Pictures/RF Sensor Full.png

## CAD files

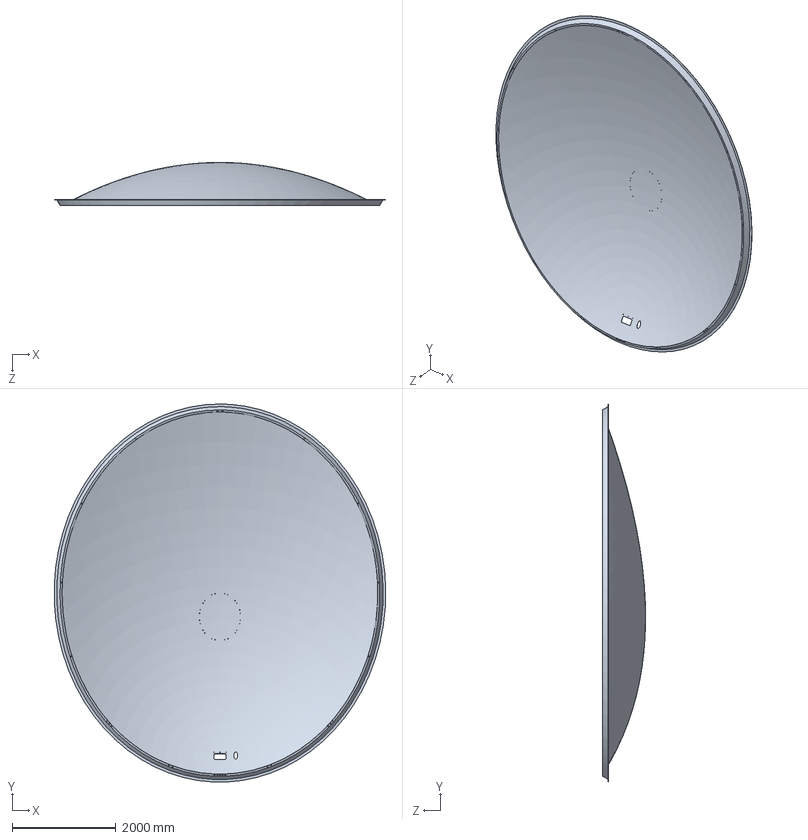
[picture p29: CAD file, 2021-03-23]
MEMOS/2019-04 Optical GRASP Model/Design Files/ATA_files/30-17-100-B Tilting Assembly/30-19-100-C Complete Assembly.SLDASM
6396.8 x 7294.2 x 833.7 mm

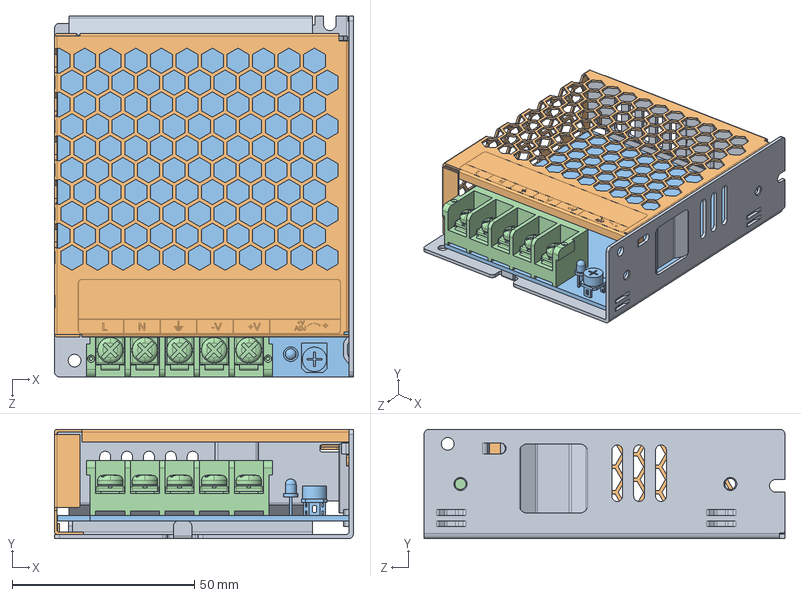
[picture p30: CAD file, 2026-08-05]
Other-Parts/NRDZ-Sensor_2026/Parts/LRS-35/LRS-35,50 Mean Well.SLDASM
82.0 x 30.0 x 99.0 mm
Bot LRS-35,50
Cap LRS-35,50
PCB LRS-35,50
Terminal Block LRS-35,50

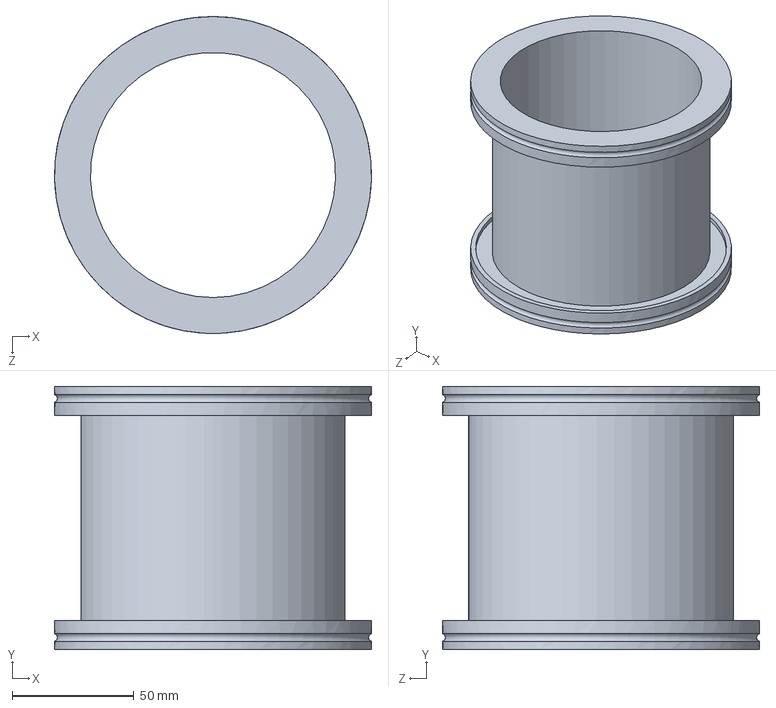
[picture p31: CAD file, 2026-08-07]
ALPACA/ALPACA CAD/Pfeiffer - full nipple, DN 100 ISO-K.SLDPRT
130.0 x 108.0 x 130.0 mm

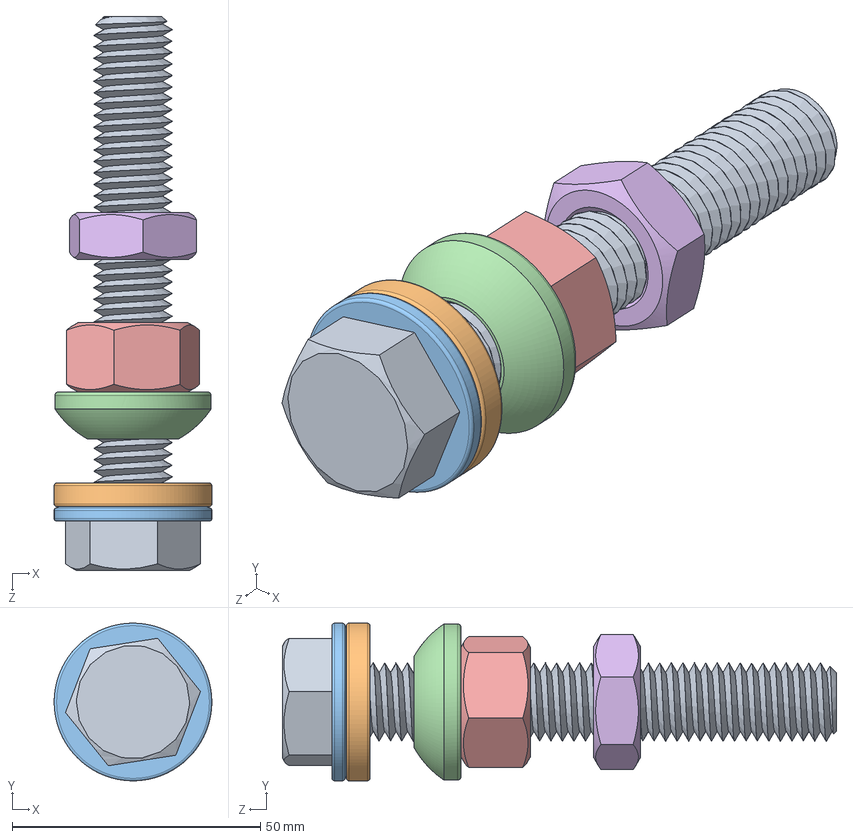
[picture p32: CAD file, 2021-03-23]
MEMOS/2019-04 Optical GRASP Model/Design Files/ATA_files/30-17-100-B Tilting Assembly/30-21-310-B Primary Node Fastener Assem.SLDASM
31.8 x 31.7 x 111.5 mm
30-21-312-A Node Bolt
30-21-313-B Washer Concave-1 set
30-21-314-B Washer Convex-1 set
30-21-317-A Washer Convex-2 node
30-21-318-A Nut hex full
30-21-319-A Nut hex jam

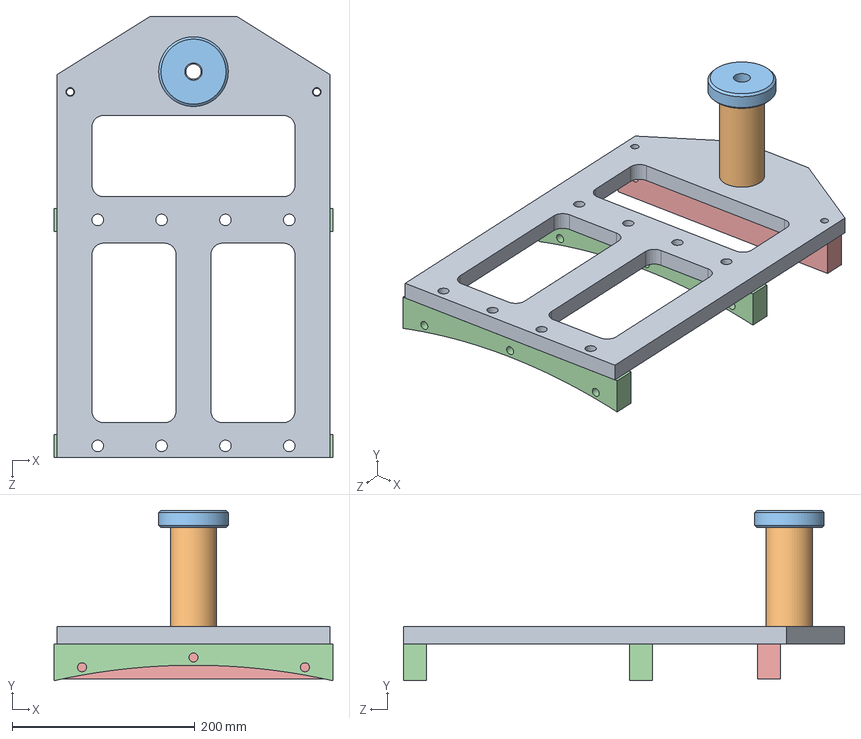
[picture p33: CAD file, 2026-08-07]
ALPACA/ALPACA CAD/ALP-CART-47 Pin Assembly.SLDASM
304.8 x 186.5 x 482.6 mm
ALP-CART-48 GBT Side Panel
ALP-CART-50 GBT Pin
ALP-CART-51 GBT Pin Cap
ALP-CART-36 GBT bracket x 2
ALP-CART-49 GBT 18 brace

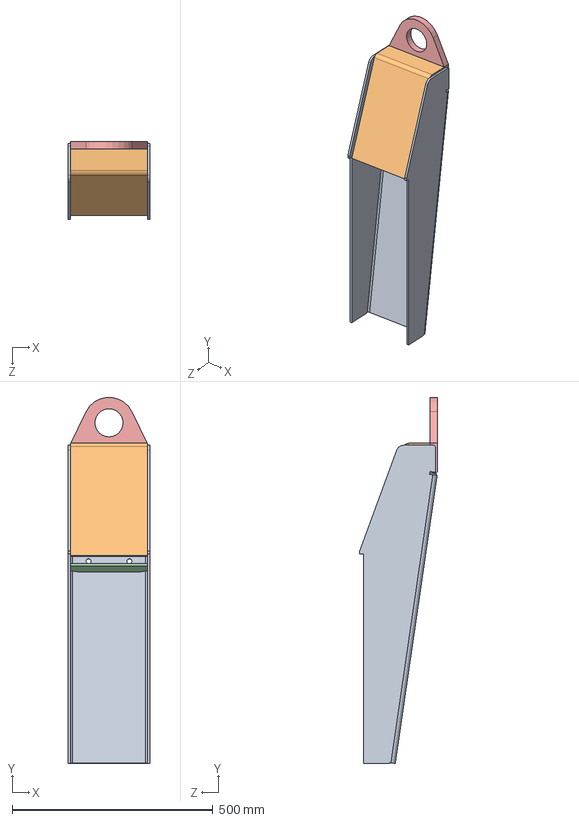
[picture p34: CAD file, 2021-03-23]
MEMOS/2019-04 Optical GRASP Model/Design Files/ATA_files/30-17-100-B Tilting Assembly/30-18-120-B Frame, Post Assy.SLDASM
203.2 x 910.7 x 193.7 mm
30-18-121-A Frame, Post, Channel
30-18-122-B Frame, Post, Top Plate
30-18-123-A Frame, Post, Gusset 1
30-18-124-A Frame, Post, Gusset 2 x 2
30-18-125-A Frame, Lifting Eye

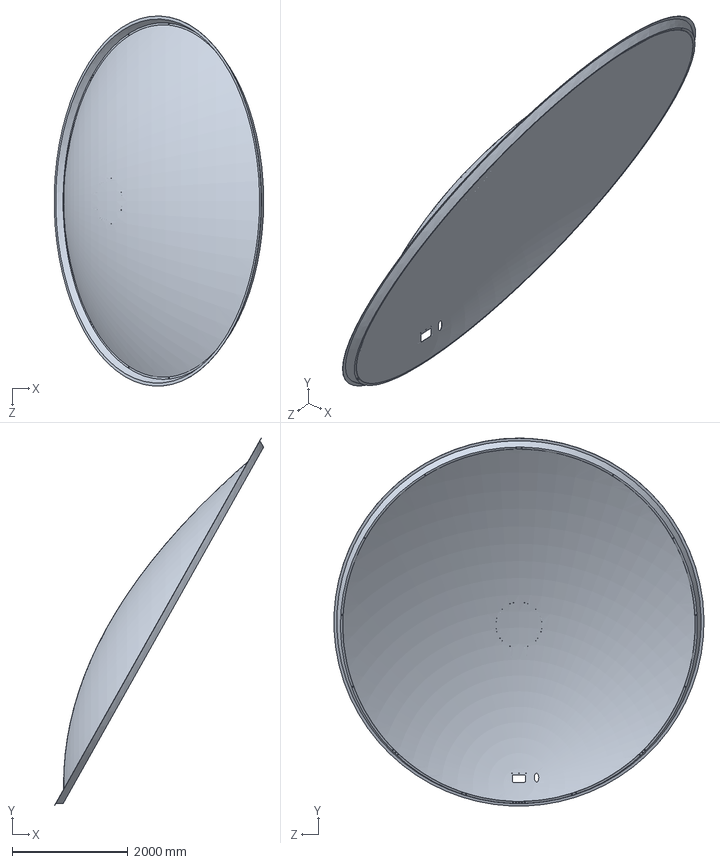
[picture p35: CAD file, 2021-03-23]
MEMOS/2019-04 Optical GRASP Model/Design Files/ATA_files/30-17-100-B Tilting Assembly/30-19-104 Primary reflector assy.SLDPRT
3620.0 x 6359.8 x 6396.8 mm

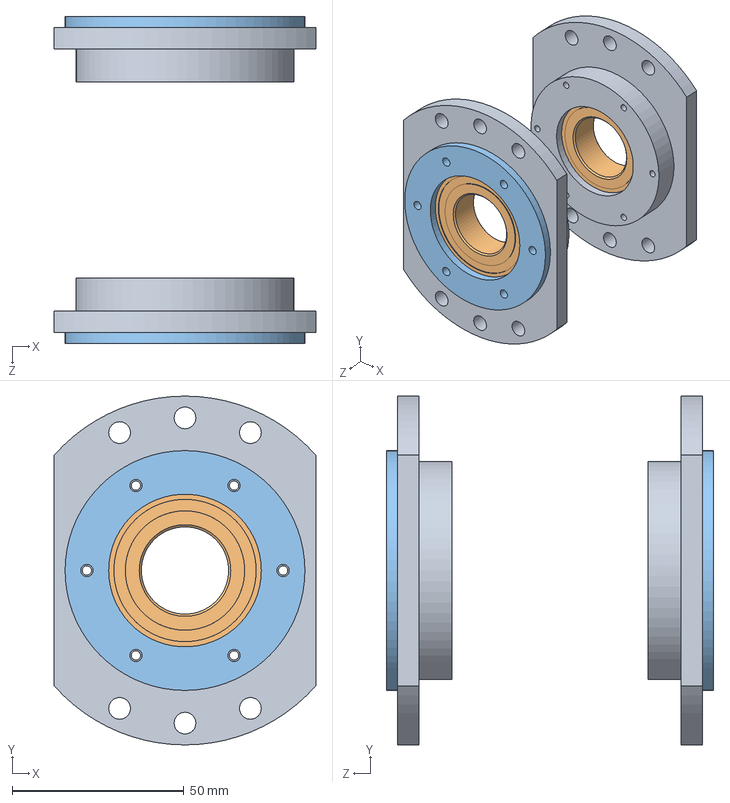
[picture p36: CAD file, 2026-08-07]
ALPACA/ALPACA CAD/ALP-CART-46 Bearing Assembly.SLDASM
76.2 x 101.6 x 95.2 mm
ALP-CART-24 Bearing mount x 2
60355K708_BALL BEARING x 2
ALP-CART-25 Bearing retainer x 2

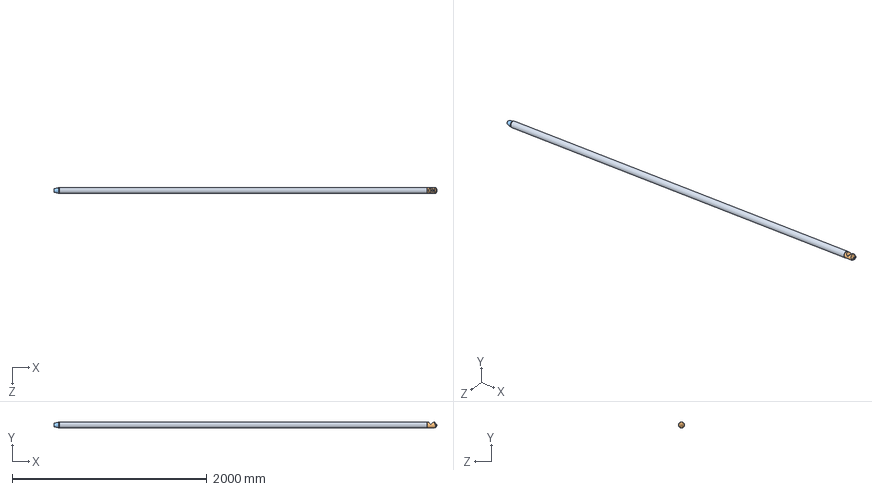
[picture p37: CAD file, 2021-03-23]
MEMOS/2019-04 Optical GRASP Model/Design Files/ATA_files/30-17-100-B Tilting Assembly/30-21-100 primary strut assem REV B.SLDASM
3931.1 x 63.5 x 63.5 mm
30-21-102-A Primary Strut Tube Extrusion
30-21-111 Strut 1 end
30-21-101 Primary strut tapered end with UPDATED LATHE FEATURES

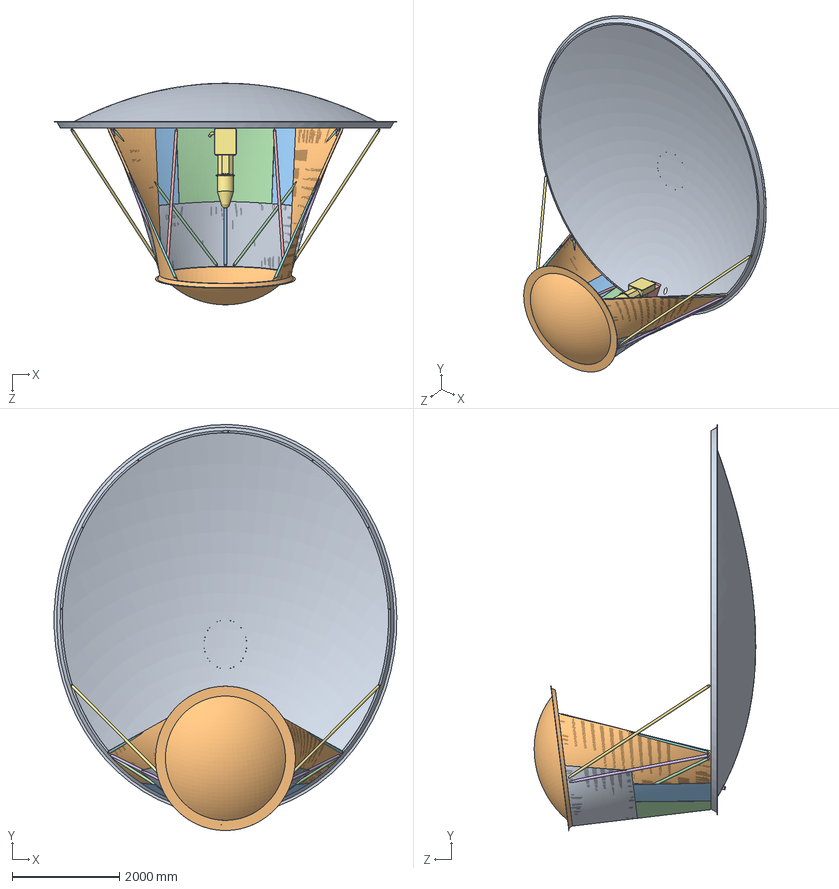
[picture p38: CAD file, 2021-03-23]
MEMOS/2019-04 Optical GRASP Model/Design Files/ATA_files/30-17-100-B Tilting Assembly/30-17-100-B Complete assembly.SLDASM
6396.8 x 7578.9 x 4136.6 mm
30-19-104 Primary reflector assy
30-20-101 Secondary reflector part
30-21-D-S0R Secondary strut
30-21-D-S2R Secondary strut x 2
30-21-D-S3R-B Secondary strut x 2
30-21-D-S4R Secondary strut x 2
30-21-D-S5R Secondary strut x 2
30-21-D-S6R Secondary strut x 2
30-21-511-2 Shroud, Center
30-21-512-2 Shroud, Upper x 2
30-21-514 Lower 2 curved x 2
30-21-548-1 Shroud, Door x 2
30-25-011 Focus Support Simple
30-25-012 Feed Mount & Slide Simple
30-29-010 Cooled Feed Outline Part

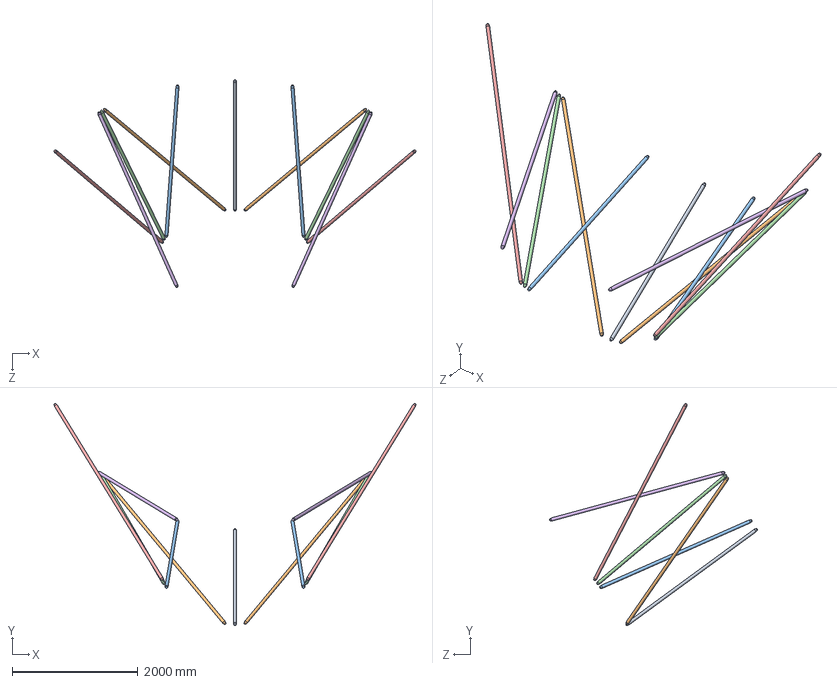
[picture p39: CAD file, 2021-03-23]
MEMOS/2019-04 Optical GRASP Model/Design Files/ATA_files/30-17-100-B Tilting Assembly/30-21-200-B Secondary struts assy.SLDASM
5768.5 x 3540.3 x 3313.2 mm
30-21-D-S0R Secondary strut
30-21-D-S2R Secondary strut x 2
30-21-D-S3R-B Secondary strut x 2
30-21-D-S4R Secondary strut x 2
30-21-D-S5R Secondary strut x 2
30-21-D-S6R Secondary strut x 2

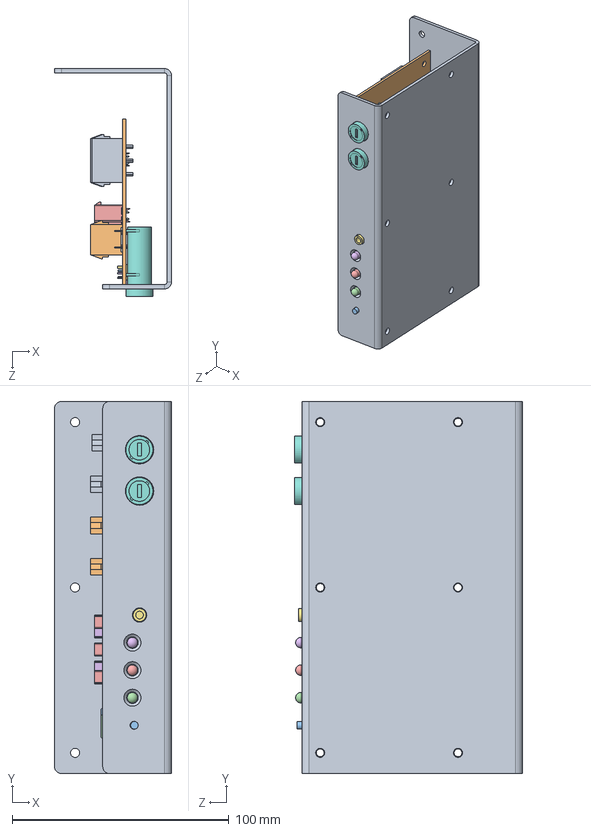
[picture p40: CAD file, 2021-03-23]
MEMOS/2019-04 Optical GRASP Model/Design Files/ATA_files/30-17-100-B Tilting Assembly/30-26-370-A Distributor Monitor.SLDASM
54.0 x 171.4 x 105.1 mm
30-26-373-A Monitor Bracket & Cover
30-26-372-A Monitor & Distribution Board
E Switch Reset
LED Yellow
LED Green
LED Red
A3 Jack
Schurter 3101-005 x 2
Molex 10-84-4030 x 4
Molex 10-84-4020 x 2
Molex 43045-0814
Molex 43045-0614
Molex 39-29-0023 x 3
Molex 39-29-0043 x 2

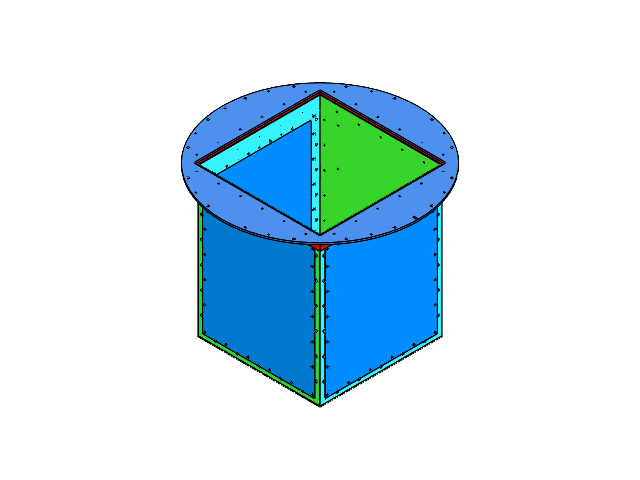
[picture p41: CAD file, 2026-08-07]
ALPACA/ALPACA CAD/FEB assembly.SLDASM
ALP-DS-T0-PF-FEB-05 - Sterling Mnt Flange
ALP-DS-T0-PF-FEB-04 - Mount Angle x 4
ALP-DS-T0-PF-FEB-01 - Box Top
ALP-DS-T0-PF-FEB-02 - Box Long Narrow
ALP-DS-T0-PF-FEB-03- Box Long Wide x 2
ALP-DS-T0-PF-FEB-08 - Bottom
ALP-DS-T0-PF-FEB-07 - Side panel x 3

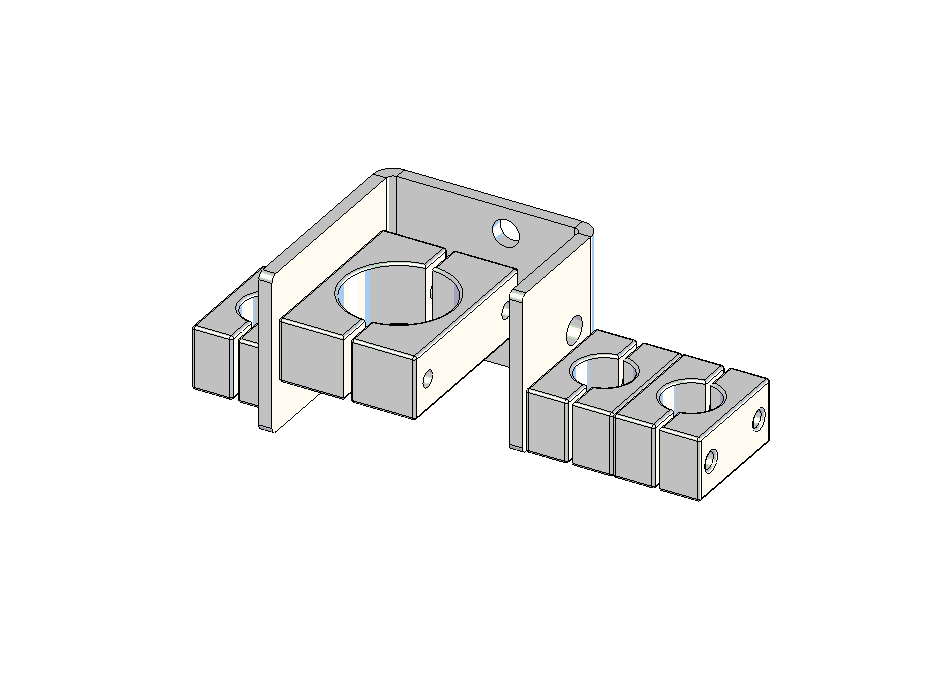
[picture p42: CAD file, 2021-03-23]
MEMOS/2019-04 Optical GRASP Model/Design Files/ATA_files/30-17-100-B Tilting Assembly/30-26-171-A Conduit Bracket Assy, U, Upper Left.SLDASM
30-26-181-A Conduit Bracket, U, Upper Left
30-26-184-A Conduit Clamp Set, 1.00, 4266 x 3
30-26-186-A Conduit Clamp Set, 2.00, 6508

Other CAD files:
Antenna/Control Documents/30-27-400 Drives/driverBoard/drive BOARD assm.SLDASM
Antenna/Control Documents/30-27-600 Front End/Front End DRD via Minex/PAX/Drawings/30-24-000 pax assem sealing lid 3.SLDASM
Antenna/Control Documents/30-27-400 Drives/driverBoard/AzElDriveBoard.SLDASM
ALPACA/ALPACA CAD/Primary Cal Split -Cal Inject Box Subassembly.SLDASM
ALPACA/ALPACA CAD/22925T110_AIR-RIDE CASTER.SLDPRT
ALPACA/ALPACA CAD/3030_14.SLDPRT
ALPACA/ALPACA CAD/3030_19_45.SLDPRT
ALPACA/ALPACA CAD/3030_31_angle leg.SLDPRT
ALPACA/ALPACA CAD/3030_36.SLDPRT
ALPACA/ALPACA CAD/3030_48.SLDPRT
ALPACA/ALPACA CAD/3030_64.SLDPRT
ALPACA/ALPACA CAD/6-way splitter.SLDPRT
ALPACA/ALPACA CAD/60355K708_BALL BEARING.SLDPRT
ALPACA/ALPACA CAD/6204K225_Heavy Duty V-Belt Pulley.SLDPRT
ALPACA/ALPACA CAD/75240a_isolator.SLDASM
ALPACA/ALPACA CAD/ALP-CART-04 Frame 3030-14.375.SLDPRT
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

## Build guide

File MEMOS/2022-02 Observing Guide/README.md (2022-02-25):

# Observation Guide

This document details using the ATA to perform observations. The contents include accessing the cameras and monitors, 
using the control machine, moving the antennas, and recording data.

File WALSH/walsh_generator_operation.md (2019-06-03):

Walsh Generator Operation:

Wal Generator operation.

During power on, J-K Flip Flop U16A is preset by U14, pin 6 (output Q) of U16A which is connected to pin 14 (input J) and pin 13 (input ~K) of U16B get Hi. Then positive transition of the clock SYNC CK (409.6 KHz) will cause U16B pin 10 changing state from Lo to Hi. As a result, a Hi to Lo short pulse is generated through circuitry (U11C, U15D, U18), which will reset the J-K Flip Flop U17A.

After U17A get reset, pin 6 (Q output) of U17A which is connected to the pin 2 (input J) of U16A goes Lo. Since both input J and K of U16A are Lo, pin 6 (output Q) of U16A will not change state and keep Hi, no matter what is the status of 1PPS clock pulse.
On the other hand, a Hi at pin 10 (output Q) of U16B will allow SYNC CK (409.6 KHz) to be the clock source for Synchronous Binary Counter U5, U9, U13 through  NAND gate U15B or U15C. Counter starts to count and there is no synchronous to 1PPS.

When reset button is press, a negative short pulse which is generated through R5, R6,C3 will preset J-K Flip Flop U17A, then Pin 6 (output Q) of U17A changes from Lo to Hi, this change will generate another negative short pulse through U11B, U12, U15A to reset J-K Flip Flop U16A, U16B and Synchronous Binary Counter U5, U9, U13.

After reset, pin 6 (output Q) of U16A goes Lo, pin 2 (input J) of U16A goes Hi, and pin 3 (input ~K) of U16A stays Hi, any positive transition of 1PPS will cause pin 6 (output Q) of U16A changed state from Lo to Hi. Then positive transition of the clock SYNC CK (409.6 KHz) will cause U16B pin 10 changing state to Hi. Once U16B pin 10 is Hi, SYNC CK (409.6 KHz) will be clock source for Synchronous Binary Counter U5, U9, U13 and start to count with positive transition of SYNC CK (409.6 KHz). 

Since 1PPS clock get in first to turn Synchronous Binary Counter U5, U9, U13 clock source on, and then counter starts to count. There is synchronous to 1PPS. 

It is noted that the counter is only synchronous to first cycle of 1PPS. After that, J-K Flip Flop U17A get reset from negative short pulse which is generated through circuitry (U11C, U15D, U18), pin 6 (Q output) of U17A goes Lo, pin 6 (output Q) of U16A will not change state and keep Hi, no matter what is the status of 1PPS clock pulse.

The power on reset is generated through J-K Flip Flop U17B. When power is on, U17B is clear by U14, pin 9 of U17B (output ~Q) goes Hi, pin 14 of U17B (input J) is connected to pin 3 of U19 (timer LM555) which is output of a Monostable mode operation. Any negative pulse input to trigger pin (pin 2 of U19) will generate a pulse with pulse width about 242 ms (t=1.1xR16xC4) at pin 3 of U19. In the mean time, pin12 of U17B (CLK2) is connected to pin 15 (Ripple carry TC) of Synchronous Binary Counter U5, it will go to Hi whenever all pin 11, 12, 13, 14 (QA, QB, QC, QD) are Hi, and will occur every 3.9ms (409.6 KHz/16). 

Since pin 13 (~K) of U17B is connected to +5V, input K is Lo all the time. The state of output ~Q (pin 9 of U17B) is based on input J (pin 14 of U17B) only. After power on, if input J (pin 14 of U17B) is Lo at positive transition of CLK2 (pin12 of U17B), output ~Q (pin 9 of U17B) does not change the state and keeps at Hi, once input J (pin 14 of U17B) is Hi at positive transition of CLK2 (pin12 of U17B), output ~Q (pin 9 of U17B) changes the state from Hi to Lo, then generates a negative pulse at pin 5 of U17 through C40 (0.1UF) to preset J-K Flip Flop U17A, operation is same as reset by press reset button. 

After output ~Q (pin 9 of U17B) goes Lo, any positive transition of CLK2 (pin12 of U17B) will not affect the state of output ~Q (pin 9 of U17B) any more, it will keep Lo all the time for the reasons as follows:
 *In the case input J (pin 14 of U17B) is Lo at positive transition of CLK2 (pin12 of U17B), output ~Q (pin 9 of U17B) does not change the state and keeps at Lo.
 *In the case input J (pin 14 of U17B) is Hi at positive transition of CLK2 (pin12 of U17B), output ~Q (pin 9 of U17B) would be Lo.

However, power on reset circuitry is generated by assuming both SYNC CLK (409.6 KHz) and 1PPS are existed. It will not work, if either one is missing during power on.

3-pin jumper J4 is used to select the rising edge or falling edge of 1PPS to clock in J-K Flip Flop U16A. It is connected to pin1 of U7A by default.
3-pin jumper J8 is used to select the rising edge or falling edge of 1PPS to trigger the timer U19. It is connected to pin2 of U7A by default.
3-pin jumper J9 and J10 are used to select the rising edge or falling edge of SYS CLK (409.6 KHz) to clock in Synchronous Binary Counter U5, U9, U13. 
For J10, it is connected to pin2 of U11A by default.
For J9, It is connected to pin 8 of U15C by default.

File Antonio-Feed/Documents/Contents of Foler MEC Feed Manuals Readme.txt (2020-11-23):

Contents of Folder:  "MEC Feed Manuals"

This folder contains the following equipment manuals:
   "ATA Cooled Feed Manual Operation & Installation" ( docx & pdf )
   Minex has been putting together this manual mainly for internal use.
   It is the basis for an improved version to be issued later. 

   "ATA Cooled Feed Manual Control Commands"  ( docx & pdf )
   Minex has put together this manual of software commands.  This is a summary of
   commands for the custom Feed Control Board and other Control boards made by
   other manufacturers.

   "Pfiffer Manual PT0208BEN_G Pump Op Inst"   ( pdf )
   This manual is for the Turbo Pump.

   "Pfiffer Manual PT0204BEN_K TC-110 OP Inst"   ( pdf )
   This manual is for the Vacuum Control Unit which is attached to the Turbo Pump.

   "Pfiffer Manual MVP-006 PU0034BEN_E Diaphram Op Inst"   ( pdf )
   This manual is for the Diaphragm Pump.

   "Sunpower CryoTel GT Manual V06"   ( pdf )
   This manual is for the Cryo Cooler.

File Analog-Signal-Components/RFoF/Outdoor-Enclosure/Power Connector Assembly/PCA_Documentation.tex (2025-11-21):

\documentclass{article}
\usepackage[utf8]{inputenc}
%\usepackage{subcaption} %Captions for subfigure?
\paperheight=297mm % A4 paper dimensions
\paperwidth=210mm
\usepackage{float}

% Manually setting page dimensions
\setlength{\textheight}{235mm}
\setlength{\topmargin}{-1.2cm} 
\setlength{\textwidth}{15.5cm}
\setlength{\oddsidemargin}{0.5cm}
\setlength{\evensidemargin}{0.5cm}

% Include more figures type: eps,pdf,jpg, png
\usepackage{graphicx}
\usepackage[table,xcdraw]{xcolor}

% Hyperlinks:
\usepackage[hidelinks,colorlinks=false,bookmarks=false,linkcolor=black,urlcolor=black]{hyperref}

\pdfminorversion=5 
\pdfcompresslevel=9
\pdfobjcompresslevel=2\pdfobjcompresslevel=2

\begin{document}
\begin{center}
\textbf{\LARGE{IP 68 Outdoor Cable assembly for 120V Mains Supply}}\\
Alexander Pollak\\
November 19th, 2025\\
\end{center}

This document describes the assembly of the IP68 rated power cord that is used to supply mains voltage (120V AC). Figure \ref{fig:completed} shows a picture of the finished cord. Figure \ref{fig:WEIPU-3P} shows the wiring diagram for the WEIPU plug.
\\
\section{List of parts and tools needed:}

\begin{itemize}
\item WEIPU Plug Female 3P Solder UL (MPN\#: SP2110/S3II-1N(U))
\item Shrink Tube HS-TBG 6.4mm BK (Mouser\#: 650-TAT125014)
\item Shrink Tube HS-TBG 3.2mm BK (Mouser\#: 650-RNF-100-1/8-BK-S)
\item Power Cord various length (MPN\#: XXXXX)
\item Solder Iron, Side Cutter, Heat Gun.
\item \texttt{[ WEIPU Rcpt Male 3P Solder UL (MPN\#: SP2113/P3-1C(U)) ]}
\end{itemize}

\begin{figure}[H]
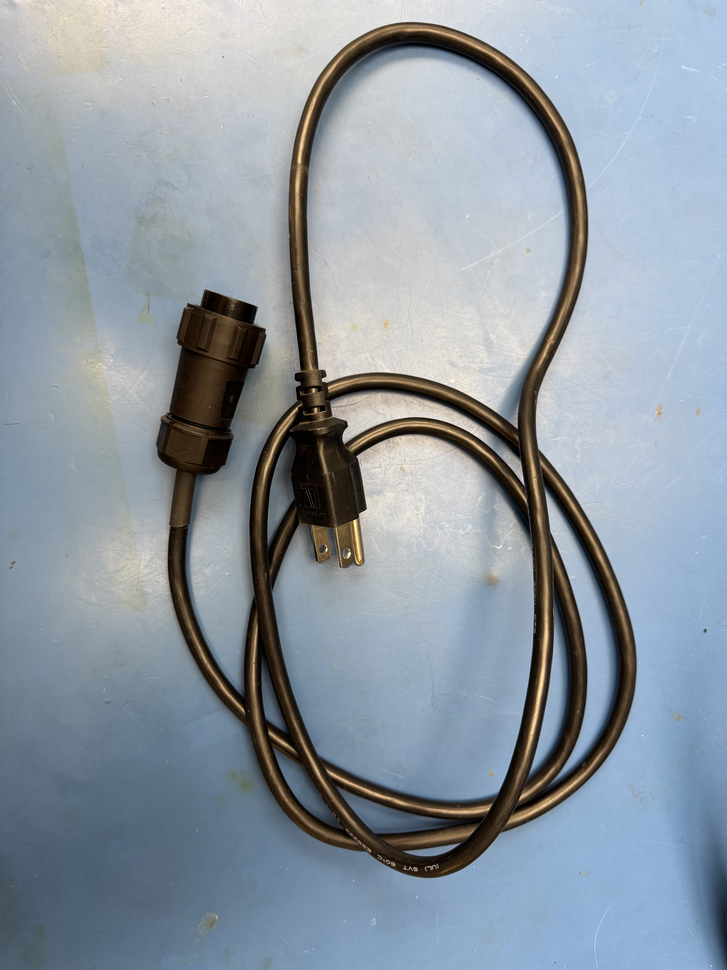
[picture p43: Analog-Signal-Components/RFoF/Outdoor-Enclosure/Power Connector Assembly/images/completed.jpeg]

\caption{Picture of the completed cable assembly.}
\label{fig:completed}
\end{figure}

\begin{figure}[H]
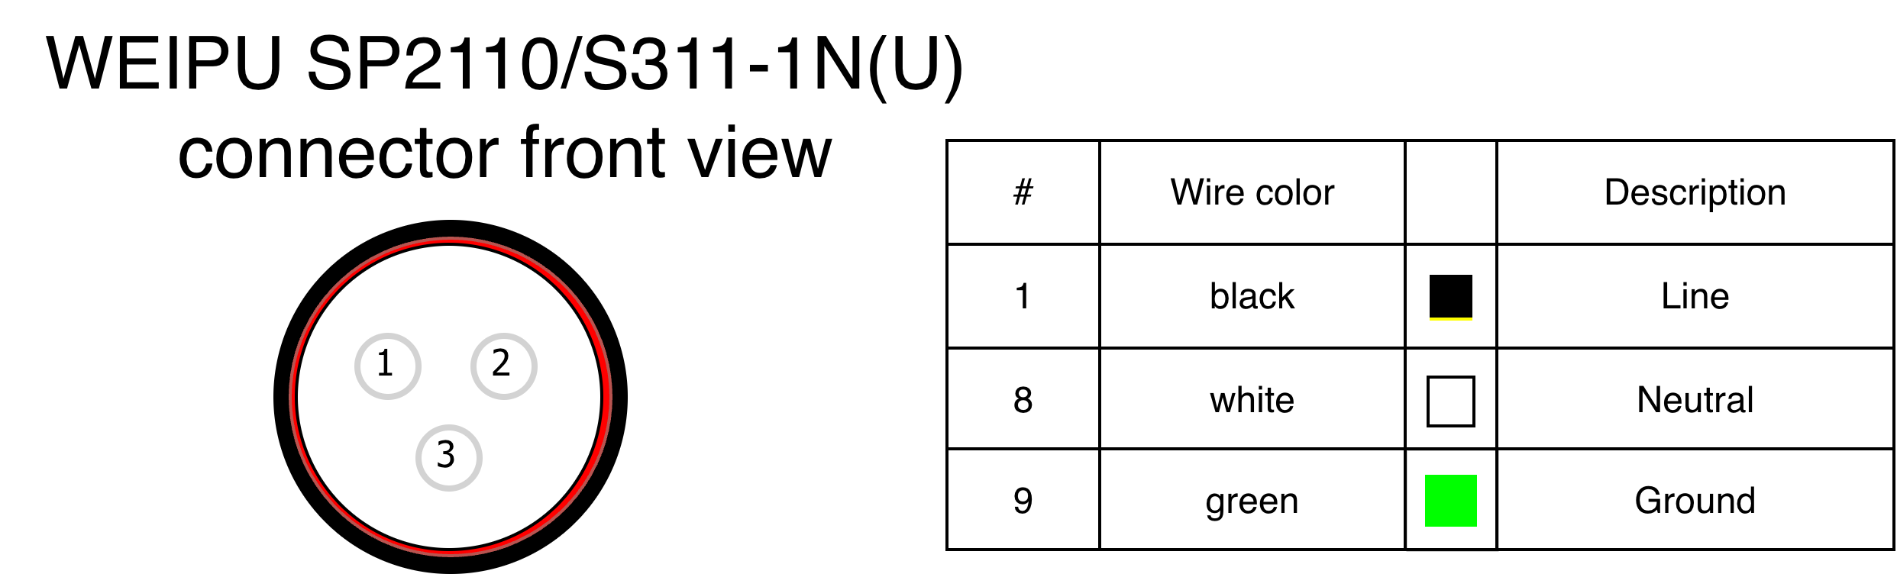
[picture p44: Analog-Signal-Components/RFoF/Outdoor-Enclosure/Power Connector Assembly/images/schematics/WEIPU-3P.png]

\caption{WEIPU 3 Pin connector wiring diagram. Note, this is standardized for all WEIPU 3P connectors and is only be used to supply mains voltage 120V AC to assemblies at HCRO. }
\label{fig:WEIPU-3P}
\end{figure}

\section{Manufacturing Instructions:}

The following section provides detailed instructions on how to prepare the power-cord assembly and the step-by-step process for assembling it.

\begin{figure}[H]
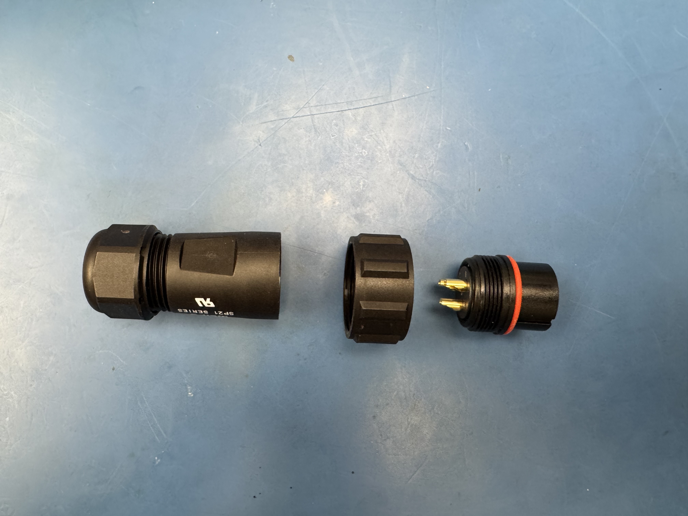
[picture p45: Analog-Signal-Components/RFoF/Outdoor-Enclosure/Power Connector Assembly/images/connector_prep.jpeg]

\caption{This picture shows the disassembled connector plug. Make sure that both parts on the left-had side are on the power cable before continuing with the assembly work. }
\label{fig:connector_prep}
\end{figure}

\begin{figure}[H]
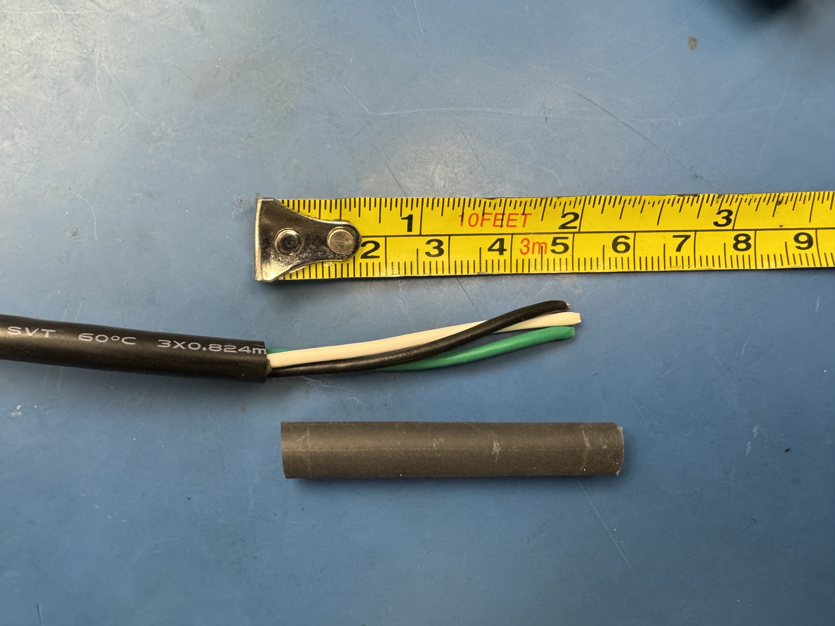
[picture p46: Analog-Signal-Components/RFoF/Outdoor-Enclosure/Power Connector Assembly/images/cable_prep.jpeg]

\caption{First, prepare the cable by removing the outer jacked at a length of about 5\,cm. Also prepare the larger shrink tube (HS-TBG 6.4mm BK) by cutting a 5\,cm long section and putting it on the power cable.}
\label{fig:cable_prep}
\end{figure}

\begin{figure}[H]
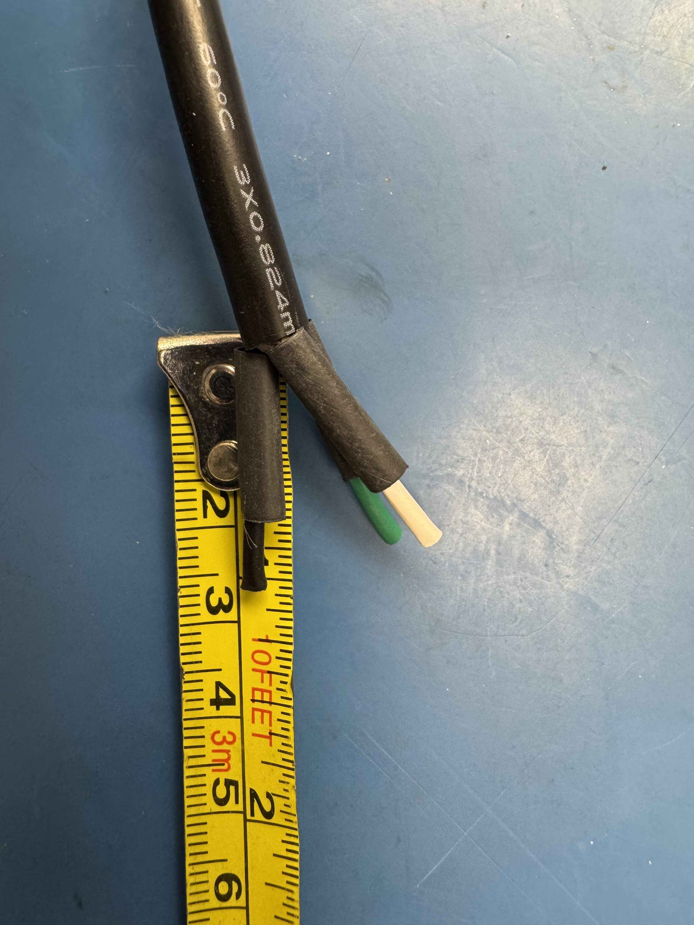
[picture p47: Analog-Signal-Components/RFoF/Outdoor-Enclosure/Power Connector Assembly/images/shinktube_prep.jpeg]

\caption{Next prepare the smaller shrink tube (HS-TBG 3.2mm BK) and cut the individual vires to the length shown in the picture.}
\label{fig:shinktube_prep}
\end{figure}

\begin{figure}[H]
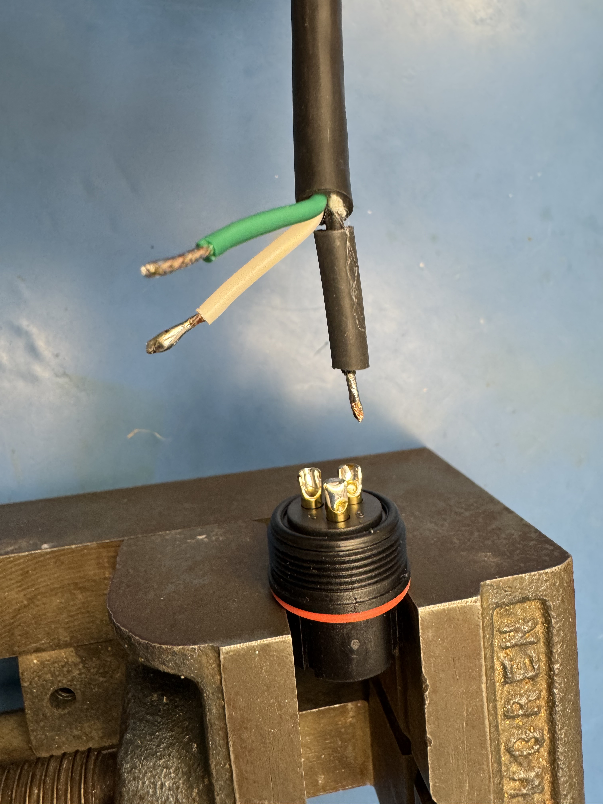
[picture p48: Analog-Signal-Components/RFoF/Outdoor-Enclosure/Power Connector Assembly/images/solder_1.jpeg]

\caption{Next, strip the wire, put solder on the wire. Put solder on the connector terminals. Put the shrink tube on the wire. Solder the wired onto the connector according to the wiring diagram in Figure \ref{fig:WEIPU-3P}. }
\label{fig:solder_1}
\end{figure}

\begin{figure}[H]
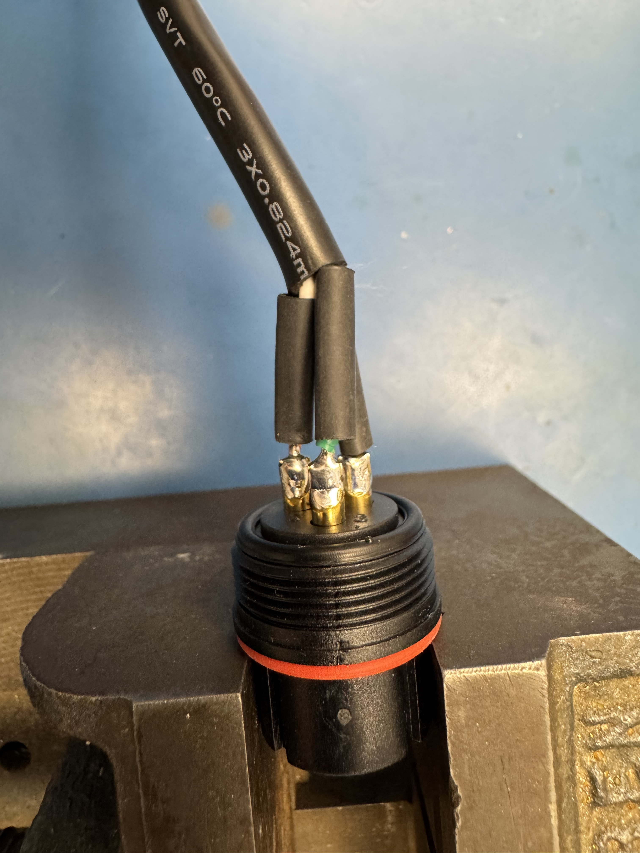
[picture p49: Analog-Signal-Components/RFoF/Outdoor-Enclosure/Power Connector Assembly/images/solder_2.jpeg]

\caption{Shows the finished soldering job. Next use the heat gun to put the shrink tube over the terminals and cable. }
\label{fig:solder_2}
\end{figure}

\end{document}

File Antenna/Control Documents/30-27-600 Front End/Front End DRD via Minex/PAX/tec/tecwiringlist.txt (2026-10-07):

/ataheat/tecwiringlist.txt

TEC driver card, linear version

Input/output list

Connector 1 - 15 pin sub D
female on board, male on cable going to power supply and PAX Case cable
all cable wires 24 ga except as noted (20 ga is 0.01 ohm/ft)

pin	function
1	NC or shield
2	PAX thermistor +
9	PAX thermistor -
3	airstream (aux1) thermistor +
10	airstream (aux1) thermistor -
4	TEC heatsink (aux2) thermistor +
11	TEC heatsink (aux2) thermistor -	  
6	supply +24 V		(20 ga wire in cable)
13	supply ground		(20 ga wire in cable)
8	TEC drive -		(20 ga wire in cable)
15	TEC drive +		(20 ga wire in cable)

Connector 2 - 9 pin sub D
female on board, male on cable to Rim Box controller board 

pin	function
1	setpoint voltage
2	rimbox heatsink thermistor monitor
6	ground
3	PAX thermistor monitor
7	ground
4	airstream (aux1) thermistor monitor
8	ground
5	TEC heatsink (aux2) thermistor monitor
9	ground

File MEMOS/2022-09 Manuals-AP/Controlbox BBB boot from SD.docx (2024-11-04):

# This document describes how to configure the BBB to boot from SD card.

## Intro:

This is required using a new BBB.

Mount boot partition and overwrite it

https://fastbitlab.com/linux-device-driver-lecture-10-making-sd-boot-default-on-bbb-by-erasing-emmc-mbr/

Dr. Alexander Pollak | SETI INSTITUTE | alexander.pollak.87@gmail.com

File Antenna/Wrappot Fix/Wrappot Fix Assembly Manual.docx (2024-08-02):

# This document describes the wiring of the Wrappot Fix V1.0 PCB

List of parts and tool needed:

- Crimp tool “Molex Microfit (#: 638112800)”
- Receptacle 3 Pos “Molex (#: 43645-0300)”
- Female Term 20-24 “Molex (#: 43030-0009)”
- Wire in black, red, yellow AWG 20

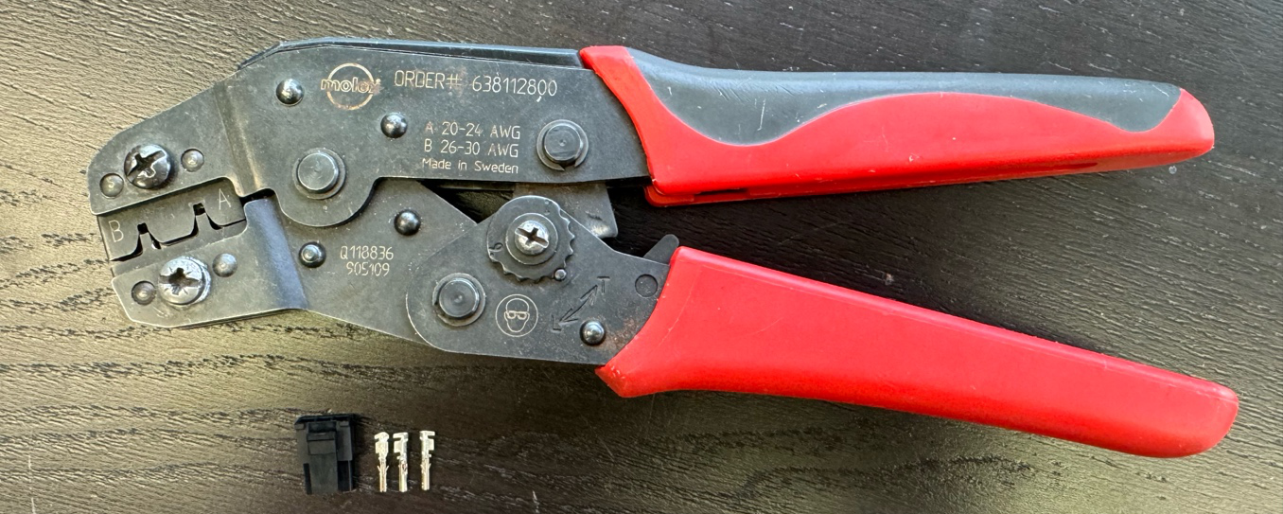
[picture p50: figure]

Wiring of PCB:

- Wire harness with 3 wires, black, red, yellow AWG 20 (twisted)
- Length between PCB and Molex connector 7.5 inch (19cm)

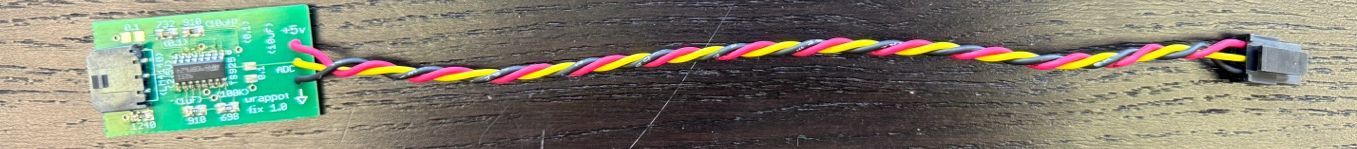
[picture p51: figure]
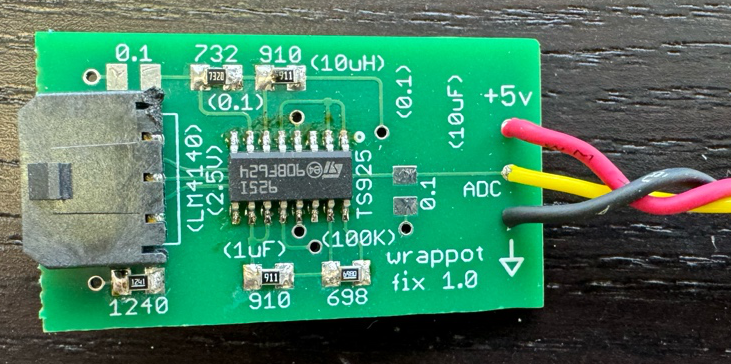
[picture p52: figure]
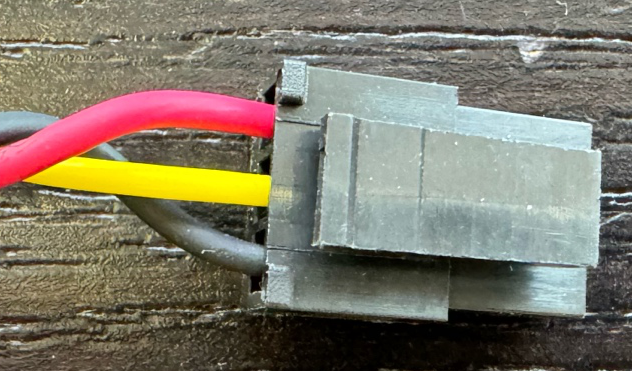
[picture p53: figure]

Dr. Alexander Pollak | SETI INSTITUTE | alexander.pollak.87@gmail.com

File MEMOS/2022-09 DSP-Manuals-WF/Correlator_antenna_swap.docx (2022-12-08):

Changing software antenna input to RFSoC correlator/beamformer

Wael Farah

v1.1

If a new antenna were to be introduced or replaced in the digital backend, a few steps are needed in order for the software to see the change.

1) Firstly, make sure that the analog (fiber/SMA) chain has been connected properly to the input of the attemplifiers and RFSoC board.
2) sudo vi /opt/mnt/share/ata_snap.tab This is the input mapping to the antenna RFSoC boards. Replace the antenna name where needed. Note that there are 2 LOs currently connected to the backend, and so the antenna will have 2 entries.
3) sudo vi /opt/mnt/share/obsinfo.toml This is the input mapping to the correlator. Replace the antenna name accordingly
4) Restart the delay engines on the observing VNC (ctrl-C, then restart)
5) (If needed) On the dsp-control machine, make sure you restart the meta-marshall service: sudo systemctl restart meta_marshall.service Sometimes the above changes does not automatically reflect in the backend, and a manual restart is needed
6) Give it a minute or so, and then check that the changes are seen in the backend by going to: http://pipeline-monitor.hcro.org:8081/ and then clicking on any node. The ANTNMSXX entries should reflect the names of the current antennas being utilized by the backend.

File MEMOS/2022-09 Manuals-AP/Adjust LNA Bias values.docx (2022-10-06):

# How to adjust the LNA bias values

## Intro:

This document describes how to adjust the LNA bias values for the Antonio Feeds. This is necessary when setting up a new feed and also periodically for all feeds in case that the values change. Note that we have two different types of LNAs installed in the Antonio Feeds and each version requires their individual voltage and current bias settings.

NOTE: A wrong bias setting can destroy an LNA, hence this needs to be done very carefully!

NOTE: Do not apply room temperature bias settings to cryogenically cold LNAs, this can lead to broken LNAs!

NOTE: Be very careful when setting up the bias level, if you are unsure about anything, please contact me and ask!

## Connect to PAX box:

## Location of code:

1 - ssh ataant@control

2 – ssh 5e

3 – telnet pax

4 – help (sometime this command needs tob e send twice )

help

help

SYNOPSIS

help [command]

DESCRIPTION

shows help information for specific PAX controller commands:

getpam - get PAM attenuator levels for X or Y channel

setpam - set PAM attenuator levels for X or Y channel

getdet - get X or Y channel power detector mean value

lnabiasoff - turn off X and Y channel Vg, Vd, and Vm

lnabiaslatch - turn on (latch) X and Y channel Vg, Vd, and Vm

getvg - get mean LNA Vg bias voltage for X or Y channel

setvg - set LNA Vg bias voltage for X or Y channel

getvd - get mean LNA Vd bias voltage for X or Y channel

setvd - set LNA Vd bias voltage for X or Y channel

getvm - get mean LNA Vm bias voltage for X or Y channel

setvm - set LNA Vm bias voltage for X or Y channel

getid - get mean LNA Id current (mA) for X or Y channel

lnabiasstore - store LNA bias settings in non-volatile memory

(getstatus) - list all LNA bias measurements and other info

gettime - get PAX controller date and time

getonboardtemp - read PAX controller temperature sensor

reset - reset PAX controller

getsoftwareversion - get version of software stored in ip2022 flash

getiposheapstatus - show statistics for ipOS internal heap

getiposnetpagestatus - show statistics for ipOS internal netpages

help - show help information for commands

Note: commands in parentheses are not implemented

EXAMPLES

show help information for getsoftwareversion command:

help getsoftwareversion

OPTIONS none prints values to stdout

## Get correct LNA information for particular feed:

First check which LNAs are in the antenna / feed, access the following file:

The _feedpartsinventory excel sheet is located at: https://github.com/SETIatHCRO/Front-Page/blob/master/Antonio-Feed/__FeedPartsInventory.xlsx

Check what feed is intalled in the antenna, then check what pyramid is installed in the feed, and then check what LNAs are installed in the pyramid.

After that locate the LNA datasheet for the corresponding LNAs, which are located here:

https://github.com/SETIatHCRO/Front-Page/tree/master/Antonio-Feed/_LNA%20SN%20Datasheets

Open the data sheet and find the LNA bias values when operated at cryo temperatures (in this example we look at the values for an IAF LNA which has a higher current setting compared to the LNF LNAs):

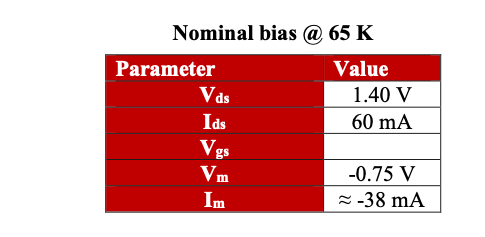
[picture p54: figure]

NOTE: IAF LNAs are marked with “F” in the excel sheet, if you apply the IAF bias settings to a non IAF LNA, this will damage the LNA!

The cryogenical bias values for an LNF LNA are following:

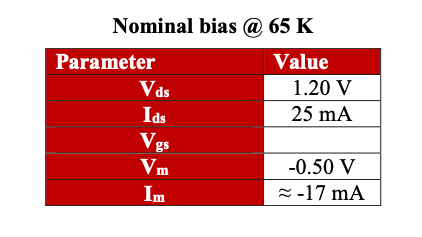
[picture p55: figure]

The QRFH prototype has different LNAs too:

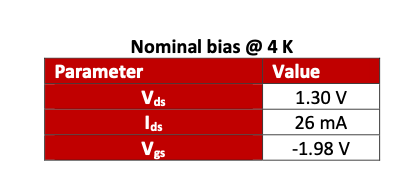
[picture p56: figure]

NOTE: The bias settings for the QRFH need to be adjusted for the operation at 70K compared to the standard data sheet!

Use following settings: Vds=1.20V and Ids=30mA

NOTE: Ids might not be reachable with the existing bias board!

## Procedure to set the correct bias level:

First: leave the LNA bias off, set the default values for the LNA via the command line (example here is for an IAF LNA):

1 - setvm x -0.75

2 - setvm y -0.75

3 - setvd x 1.4

4 - setvd y 1.4

5 - setvg x 0

6 - setvg y 0

Now switch on the bias supply and read back the values:

7 - lnabiaslatch

8 - getvm x (-0.73)

9 - getvd x (1.33)

Now adjust VD and VM for X and Y so that when reading back the values they show the correct voltages, by using setvm and setvd!

Next read the drain current and adjust VG so that ID equals the correct value.

10 - getid x (56.4)

11 - setvg x 0.2

…

12 - getid x (59.4)

13 - setvg x 0.12

…

14 – getid x (60.0)

Repeat for Y pol.

Finally read back all values and double check that all of the are correct:

15 - getvm x (-0.75)

16 - getvd x (1.4)

17 - getid x (60.0)

18 - getvm y (-0.75)

19 - getvd y 1.4)

20 - getid y (60.0)

When all values are correct store the settings!

21 - lnabiasstore

The exit the terminal.

22 - ^]

## Set PAX Box antenna mapping in SQL data base:

1 – ssh root@data.hcro.org

2 – mysql

3 – SHOW DATABASES;

4 – USE atadata;

5 – SHOW TABLES;

6 - select ant, pax_box_sn from feed_parts; (show existing mapping)

7 - update feed_parts set pax_box_sn ='PB-010' where ant='5e'; (map PAX 10 to antenna 5E)

8 - update feed_parts set pax_box_sn ='NULL' where ant='5e'; (remove existing mapping)

9 - select ant, pax_box_sn from feed_parts; (check new mapping)

10 – exit;

## Set PAX Box antenna mapping in Json file data base:

1 – ssh atasys@control.hcro.org

2 – cd /hcro/atasys/ata/etc/

3 - nano ants.json

Adjust all values, like PB number, Feed Number, DB and CB numbers to the correct installed components.

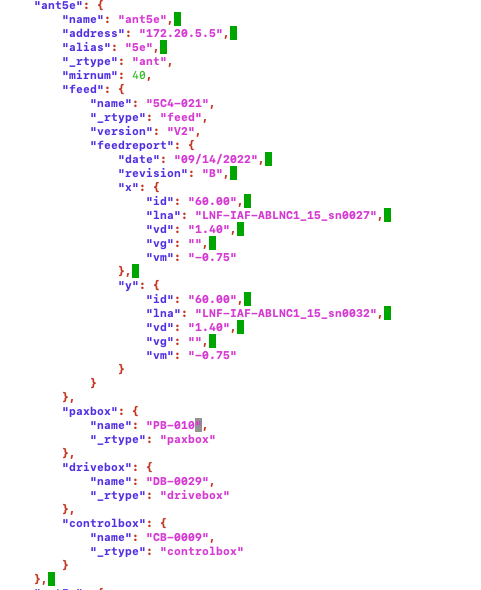
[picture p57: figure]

Dr. Alexander Pollak | SETI INSTITUTE | alexander.pollak.87@gmail.com

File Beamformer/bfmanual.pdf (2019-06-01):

# The Allen Telescope Array Beamformer

## Concise Operational Guide

## “Forming better beams since 2008”

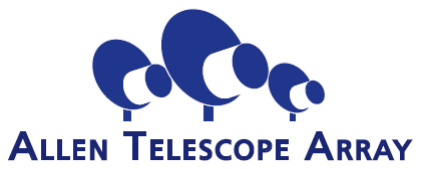
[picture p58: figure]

William C. Barott, PhD
For the SETI Institute

Document revised on 5/17/2012

Questions, comments, or other inquiries, contact author Billy Barott barottw@erau.edu

## Summary and Introduction

Calibration. Pointing. Tracking. Interference nulling.

This document contains user-level instructions on operating the ATA beamformer. At its heart, the beamformer is a rather simple instrument: Pick a direction on the sky, form a beam, and if you’re ambitious, null some interferers in the process. The major functions required before observing are initialization and calibration.

The following pages give a description of the major beamformer functions and examples of how to use them, with the hope of getting a new user “on-air” as quickly as possible. Additionally, advanced information is available for those who wish to take the beamformer a bit further. Power-user information takes this a step further for those who wish to delve into the full customizability of the beamformer.

The beamformer’s primary capability is to form four discrete single-polarization beams anywhere on the sky. Additionally, it can serve as a spectrometer with its built-in 16,384-channel auto-correlator (6.5 kHz resolution) on each branch node. Additional capabilities include N cross-correlation spectra and N auto-correlation spectra, each of which can be written to disk. Diagnostic capabilities include logging and writing various link-related data to the disks.

This document is maintained on log.hcro.org under the beamformer systems page.

## Recent Major Changes

May 2012
The main elements of this update are to introduce the syntax for the SonATA packetizer commands and control and to add detail about more-advanced diagnostic and troubleshooting switches.

December 2008
Several major changes were introduced in the Dec 21-30 upgrades. These are summarized below (see the full documentation for details).

Circular Polarization: Single-pol beam processors now terminate in a CP concatenation stage. By default, this stage is ignored during calibration and the linearly polarized beams pass through unchanged. See new flags (ie, pol, calpol) to activate this stage.

New Beam Calculator: The engineering beam calculator group has been moved to the standard library, and a new beam calculator beamPhasedPolBias has been added. It functions similarly to beamDefaultPhased except that it adds the degree-value of the variable polbias to all inputs identified as “y” polarizations. The purpose is to provide a simplified source polarization model during calibration, and this calculator should not be used for observing.

DAC iBob Control: The bfibob script now has options for the DAC iBobs. It is necessary to run bfibob with the dacinit option to tune DACs to the correct beam. This must be done after each physical power-up (recommended to run at the same time as bfibob walsh). The option dacstatus gives some status information about the DACs.

Peak Register Display: Peak registers give one output per beamformer rather than one per beam processor. This is by design to keep the single-pol beams at the same relative gain levels. The reported value is the maximum of the two single-pol beams.

Reference Antenna Selection: The method of refant selection has changed from an independent node-by-node analysis to a holistic analysis of the entire beamformer. This change facilitates scored refant selection based on noise temperature. Additionally, the beamformer prohibits combinations resulting in the correlation of two inputs from the same antenna (i.e., 1ax with 1ay).

Noise Temperature Inputs and Alarms: The file ata.tsys stores noise temperature data for each input and is now read during initialization. BFTrackepehm will now alarm out of range noise temperatures in the same manner that it alarms calibration errors. These alarms and warnings are generated from Tsys thresholds relative to the best-performing antenna in the hookup.

A Few Commands to Look At: See documentation for the following commands: --calpol, --pol, --specsrc, --specshift, --corrsb, dacinit, dacstatus

Tutorial for Circular Polarization
The following procedure can be used for circular polarization calibration.
1. Select a calibrator and determine its phase offset. This phase offset is critical: It determines the expectations of the source and ultimately whether the beamformer will indeed produce circularly polarized beams when it is done. For example, strong circular sources would be +/- 90, and linear sources 0/180. The degree of ATA cross-pol isolation might result in source-dependent tweaks.
2. Calibrate the beamformer using the beamPhasedPolBias calculator. Remember that circular calibrations generally take longer, since sources are weakly polarized or unpolarized. There’s not yet a good sense for how much longer.

bftrackephem.rb -b 1 -f 1420 -e calibrator.ephem -i 10 --caldelay Old
--calcp | New: Enables calibration of CP top node.
--bctype beamPhasedPolBias | New: Sets the beam calculator to the CP helper.
--bcvar polbias=X | New: Sets the pol bias for the bc, where “X” fits your source.
3. Observe using beamDefaultPhased (or your favorite calculator) configured for circular polarization.
bftrackephem.rb -b 1 -f 1420 -e target.ephem | Old
--pol circular | New: Selects circularly polarized output
--bctype beamDefaultPhased | New: Set your calculator back to normal
4. Done!

## Table of Contents

Summary and Introduction | 3
Recent Major Changes | 4
Table of Contents | 6
The iBobs: Setup | 7
Phase Switching (walsh functions) | 7
Data Source Selection | 7
Attemplifier Control | 7
DAC Control | 8
Beamformer Initialization | 9
Basic Arguments | 9
Simple Example | 9
Advanced Arguments | 9
Example implementation: | 10
Beamformer Tracking | 11
Basic Arguments | 11
Simple Example | 12
Advanced Arguments | 12
Observational | 12
Diagnostic | 14
Power User Arguments | 14
Example Implementations (*Older) | 19
Return Codes | 21
Software Daemons | 22
Indicator Lights | 23
A User’s Checklist | 24
Output file format | 25
Programming Beam Calculators | 26
Objects accessible from the Beam Calculator | 26
Sample Code | 27
Selected Documentation for Beamformer Objects | 33
Class VALUEARRAY (selected methods) | 34
Class ANTENNAHOOKUP (selected methods) | 36
Other Matters | 38

## The iBobs: Setup

Prior to any observing or tests, the beamformer iBobs must be prepared. The script bfibob accomplishes this task, and has many functions, divided into several categories. It is located in the /home/obs/ruby/bin directory and is included in the path of the obs account on most machines. The general syntax and commands are detailed below.

bfibob [beamformer] [command] [options]

status
Verifies communications and shows the walsh and source settings.
Phase Switching (walsh functions)

walsh
Applies phase switching to all iBobs. Required if the analog walsh function generator is enabled.

nowalsh
Turns off the phase-switching circuitry of the iBobs

rearm
Resynchronizes the iBob internal clocks with 1pps
Data Source Selection

sky
Configures the iBobs to output sky data from the telescopes

fs
Configures the iBobs to output sine wave data

noise
Configures the iBobs to output pseudo random sequences of data

reseed
Commands the iBobs to synchronize their random sequence generators. Required for the noise from multiple iBobs to be coherent.
Attemplifier Control

autoatten [level]
Commands the iBobs to auto-adjust their inputs, seeking an RMS sample value of [level]. If level is omitted, a value of 11 counts RMS is sought.

getatten
Displays the current attemplifier values for all iBobs

adcstats
Displays the current ADC counts (rms input level) for all iBobs

DAC Control

dacstatus
Retrieves the current status report for the DAC iBobs on the current beamformer. Displays selected channels as well as link status.

dacinit
Initializes the DAC iBobs to draw data from the correct streams. DAC #1 receives X/Right and DAC #2 receives Y/Left. Resets link status registers.

## Beamformer Initialization

The beamformer must be initialized prior to use or any time the hookup is changed (by rewiring or changing which antennas are used in the observation). To initialize the beamformer, ssh to a user terminal (like user1) and use the following command.

/home/obs/bbarott/bfu/bfinit.rb [args]
Basic Arguments
-a [antenna list] | --ants [antenna list]
Specifies the list of signal paths to enable. Names should be comma separated and follow the ATA format, plus dupe codes (e.g. 5gx1). Partial names are allowed, so “1a” will enable all hookups beginning with 1a.
-b [beamformer] | --beamselect [beamformer]
Selects one of two beamformers (1 or 2) to initialize.
Simple Example
To initialize beamformer #1, enabling the antennas 1a,1b,1cy. The partial naming for 1a,1b will enable both polarizations (x and y) but the specific naming on 1cy will only enable the y polarization. It will be necessary to calibrate before observing.

> bfinit.rb –b 1 –a 1a,1b,1cy
Advanced Arguments
-r [antenna list] | --remove [antenna list]
Removes the list of antennas from the hookup. Allows partial names. Implies --preserve.

--preserve
Specifies that modifications are made without reinitializing the beamformer. When used with –a, the antenna list is added to (rather than replacing) the current antennas in the hookup. While this command preserves calibration data, it is possible for instrumental link delays to change as firmware is still re-loaded.
-h [value] | --headroom [value]
Controls the linear headroom for the automatic gain controller, which itself is invoked in bftrackephem. Time domain samples have magnitudes between 0.0 and 1.0. The AGC scales data so that the peaks have a value of 1.0*value. For example, a value of 0.75 (the default, if –h is omitted) means that data will be scaled to have peak values between -0.75 and +0.75, leaving the range between 0.75 and 1.0 as white-space headroom reserved for gain variations or RFI.

Example implementation:

bfinit.rb –b 1 -a 1ax,1bx,1cx,1dx Please see the hookups as previously distributed. All currently hooked-up antennas and iBobs are currently supported.
Power User Arguments

--bandwidth [new fractional bandwidth]
Changes the beamformer’s operating bandwidth, as defined by the fractional delay filter.
Packetizer Arguments
The beamformer is now integrally linked with the Sonata packetizer system. While the two operate under separate daemons, control is integrated through the bfinit and bftrackephem interfaces.

--spk
Command the SonATA packetizer to be invoked and initialize. If omitted, the passthrough firmware is installed instead. When using the packetizer the destination addresses should be set with the ip switches.
--ip0 [IP:PORT] | --ipr [IP:PORT] | --ipx [IP:PORT]
Set a destination for the stream0 data in the beamformer output stream for the SonATA packetizer. These switches are synonymous and have no discrete meaning since the beam definition calls for both “x” (in linear mode) and “r” (in circular mode) to be stored in stream0.
--ip1 [IP:PORT] | --ipl [IP:PORT] | --ipy [IP:PORT]
Set a destination for the stream1 data in the beamformer output stream for the SonATA packetizer. These switches are synonymous and have no discrete meaning since the beam definition calls for both “y” (in linear mode) and “l” (in circular mode) to be stored in stream1.

## Beamformer Tracking

The bftrackephem command directs the beamformer to either calibrate or observe (in a sense, calibration is just observing with self-adjustment). This command can be executed from the same machine as bfinit.

/home/obs/bbarott/bfu/bftrackephem.rb [args]
Basic Arguments
-b [beamformer] | --beamselect [beamformer]
Selects one of two beamformers (1 or 2) to use for observing. Required.
-f [frequency] | --freq [frequency]
Sets the beamformer and ATA sky frequency (enter in MHz). The sky frequency is software-limited at 15 GHz. If omitted, the beamformer will use the last sky frequency set with –f (1420 at initialization). Note that the beamformer can only learn of a sky frequency setting from this command, and does not use the current LO oscillator setting to determine sky frequency.
-e [filename] | --ephem [filename]
Specifies the ephemeris file for the observation. Format is the same as that generated by ataephem. The path may be relative, but must be on a file system mapped by boot2 (e.g. /home/obs). The colon character [:] is not a valid file name character, and its presence will change the function of this command (see advanced functions).
-d [duration] | --duration [duration]
Sets the duration of the observation, in seconds. Ephemeris is padded up to 100 seconds on each side. Unless overridden by –n, bftrackephem will not terminate until this duration has elapsed. Pointing data is preloaded, so long values of –d might cause a long delay before tracking starts. If not specified, this will attempt to choose a magic number based on the calibration, integration, snapshot write, and number of iteration switches. Omitting -d is not recommended for modes other than calibration. See the quickload switch for instructions on conducting long observations.
-n [cycles] | --num [cycles]
Overrides the duration with respect to how long the beamformer operates. The beamformer will only perform software updates cycles times before terminating. Does not modify the loaded ephemeris. Software limited to be between 1 and 1000; settings outside this range revert to 3.

--caldelay / --calphase / --calfreq / --calamp
Causes a calibration cycle to occur, defaulting to 3 iterations unless overridden by –n. Here, -d applies to each iteration individually. Modes include: caldelay (delays and phases), calphase (phases only, assuming no delay errors), calfreq (phases only, offset from calphase frequency), calamp (balance amplitudes, use with short integrations). All modes imply automatic snapshots.
-i [time] | --integrate [time]
Specifies the integration time, in seconds, for snapshots and calibrations. See advanced memtimer for use with non-calibrating snapshots.

--agcdb [decibel output level]
Implements the automatic gain controller. Argument is dB relative to full-scale range (determined by bfinit –h). This is usually negative or zero. Note that digital clipping levels are +/-127, with an analog range of 2 volts peak to peak. The AGC is executed based on the last snapshot, and must be used in conjunction with a calibration. AGC gains are persistent. Simple Example
To start beamformer #1 on an observation. Set the sky center frequency to 1420 MHz and load 10 minutes of ephemeris from the file indicated (relative to the current path).

> bftrackephem.rb –b 1 –f 1420 –d 600 –e ../myephem/mystar.ephem To start beamformer #1 on a delay calibration. Set the sky center frequency to 1420 MHz and load 5 minutes of ephemeris for each of three iterations on casa. Integrate for 10 seconds, and adjust the AGC during each step to try to achieve -3dB-pk output levels.

> bftrackephem.rb –b 1 –f 1420 –d 300 –n 3 –e casa.ephem
| –-caldelay –i 10 --agcdb -3
Advanced Arguments

Observational

--azel [az,el]
Alternative method of specifying pointing (versus –ephem). Comma separate (no space) the azimuth and elevation coordinates (degrees). This argument is being depreciated in favor of –e [az:el] below. It is not recommended for new scripts, and will soon be removed.
-e [az:el] | --ephem [az:el]
There is a short-cut for making –e implement fixed-position pointing. This shortcut is required for beamcalc pointings, which have no separate azel command. Use a colon [:] to separate azimuth and elevation. For
example, --ephem 40.1:23.5 acts like --azel 40.1,23.5

--write [mode]
Records and writes data snapshots to the disk. Modes include “out” “crosses” and “autos” and only one may be selected. Data is saved to the file atabf.bfs in a time-stamped directory for each activity. All data is stored under /opt/bfu/data/ on boot2.

--memtimer
Implements software coefficient updates during write cycle integrations. When omitted, coefficients are not updated (leading to errors during long integrations). Only optional for --write; calibration integrations enable the memtimer mode by default.

--sideband [sideband choice]
Changes the output mode. Valid choices are “upper”, “lower”, and “off”. This argument is persistent, and the power-up state is “off.” The “upper” mode centers the sky frequency at DC and increasing frequencies are higher sky frequencies. The “lower” mode centers the sky frequency at DC and increasing frequencies are lower sky frequencies. See --specshift for modifications to this. Persistent.

--specshift
An augmentation to sideband (can only be used when --sideband is present in the same call). Commands the beamformer to implement the 26.2144 MHz spectrum shifter. In sideband mode “upper,” the sky-frequency has a baseband value of 26.2144 MHz. Radio frequencies above Fsky are present above this (flipped in “lower”). --specshift has no effect when setting sideband “off,” and is persistent until the next --sideband call.

--offsetaz [offset]
--offsetel [offset]
Adjusts all pointings loaded during this cycle by the indicated offset, in degrees. Affects ephemeris tables and fixed pointings loaded with ephem and bcephem, but not with azel.

--timer [interval]
Causes the BEE processes to autonomously update coefficients with the given delay (in seconds) between updates. Releases control to the O.S. after starting the timer.

--quickload
Enables just-in-time beamforming. Normally, all table coefficients are calculated before the first beams are formed. For long observations this may create too much “startup” overhead, or may make the tables too large. JIT beamforming creates coefficients on-the-fly in updates at predetermined intervals. When the end of the current table is approached, old data is purged and new data is added. Note: JIT/BF is invalid for calibration cycles, and windows are scaled for integration times. If used in conjunction with –timer, data tables are updated in the background.

--pol [polarization choice]
Changes the polarization selection on the beamformer output. Valid choices are “linear” and “circular”. In linear, concatenated output streams will contain X/Y data. In circular, data is R/L. It is important that the user ensures proper calibration of the X/Y beams with each other by using calcp on a polarization-supporting source. Persistent.

--calcp | Synonym: --calpol
Optional flag to allow analysis of the circular polarization (top-level) beamformer node. If omitted, all correlation analysis (including calibration) is restricted to second-tier and below, i.e. within co-polar nodes. When included, the beamformer will analyze correlations of cross-polarized x/y tiers, allowing for alignment and (possibly) combining of these streams into right/left streams. Not sticky. Note that this flag should not be used during observing, only during calibration for cp.

--calrevert
Reverts calibrations to the “power-on” state, removing any user-observed calibration coefficients. Used to recover from catastrophic calibration failures (such as interference effects on delays, or bad antennas causing amplitudes to collapse).

--beamephem [beam,filename]
Loads unique ephemeris to each beam group. Argument is an ordered list of beam group names and ephemeris files (or fixed pointings). All beam groups and ephemeris should be entered, separated by commas. Beam group names are the polarization and duplicate identification code for antennas in the hookup. For example, antenna “2ax1” belongs to beam “x1.” Note that –ephem by itself writes to all beamgroups identically.

--beamazel [beam,az,el]
Similar to azel and beamephem. Give ordered triples of beam groups and azimuth/elevation directions, separated by commas.

Diagnostic

--statusonly
Prints the last-determined array health status to the screen and then terminates. This output is lengthy and content is subject to change.

--calalarms [type]
Commands normal snapshot writes, if invoked with –write, to assert calibration alarms (but does not adjust calibration offsets). Types are “delay” or “phase” to correspond to “caldelay” and “calphase” alarms.

--clearalarms
Resets link-related alarm conditions in the beamformer, so they will no longer be reported unless a new event occurs. Recommended only after the user has addressed the alarm condition to verify valid calibration. Power User Arguments

--bandwidth [new fractional bandwidth]

Changes the beamformer’s operating bandwidth, as defined by the fractional delay filter. This does not affect sample rate. The startup bandwidth is 0.7 (70%). Analog users may specify 0.5 for improved accuracy with no loss of output signal bandwidth. This is persistent. The calibration correlators currently require a value of at least 0.4 unless set otherwise with --calbw.

--agclin [linear output level]
An alternative to agcdb using a linear voltage scale. Equivalent with an argument of 1=0dB, 0.5=-6dB, etc. Values greater than 1 might result in clipping the output. This switch is persistent and absolute.

--gainadjustdb [decibel adjustment]
Adjusts the power gain of the output stage. Arguments are relative dB adjustments. For example, a value of -3 will decrease the power out of the beamformer by half (and is equivalent to gainadjustlin 0.707). Persistent.

--gainadjustlin [linear adjustment]
Adjusts the voltage gain of the output stage. Arguments are multiplicative relative adjustments. For example, a value of 1.2 would increase the gain by 20 percent. Persistent. Use with care to ensure no clipping.

--bctype [string]
Changes the type of beam calculator used in processing. This will affect the entire beamformer. Persistent. The primary style of beamforming is beamDefaultPhased. It is noted that the beamformer automatically forces the bctype to beamDefaultPhased when a calibration is invoked.

--bcvar [array]
Allocates variables to beam calculators. Separate variable names and their values by the “=” character, and sets of variables by commas. For example, --bcvar nullaz=40,nullel=20. Text assignments are permissible, with the exception of reserved characters. The value “nil” (no quotes) may be used to clear a variable, as in –bcvar rfi=nil. Note that “ephemeris” is a reserved name, and should not be used. Persistent.

--bcephem [array]
Loads ephemeris files into the beam calculator. A functional fusion of bcvar and ephem, with rules from both applying. For example: --bcephem null0=xm.ephem,null1=20:41.2. Ephemeris tables are persistent between calls to bftrackephem, but are only loaded for the interval given by -d. Variable names are shared with bcvar, so there cannot be duplication.

--bclib [library file]
Loads the given library file into memory so that it can be accessed by the beamformer. Loads are persistent and repeatable, and may override (but not delete) previously loaded code. File names must be relative to the current path. Use commas to separate library names.

--bcclear
Removes all beam-calculator variables from memory (as set with bcvar or bcephem). Does this prior to bcvar/bcephem directives in the current call.

--calbw [bandwidth]
Sticky. Sets the integration bandwidth for calibrations. This should be a value less than 1. As a point of reference, the power-up value is 0.4 (40% of the band), and this must be less than the value set with –bandwidth (or less than 0.7 if –bandwidth was not used). Higher values mean lower integration times but at the expense of possibly including more RFI.

--caloffset [offset]
Sticky. Sets the offset of the calibration’s integration band relative to the center of the band. This has a range of -0.5 to +0.5, but it should be noted that this must be selected with care along with calbw. IE, if caloffset is 0.4 and calbw is 0.3, the software will try to integrate from 0.25 to 0.55 – not just outside the range of the filter but also entirely outside the range of the spectrum. Proper use of caloffset and calbw can allow the user to select calibration frequencies to avoid RFI. Note: Positive values move the calibration center to frequencies above the sky frequency.

--calstronglock
Not Sticky. For the current phase cal, causes the beamformer to “lock on” to the dominant frequency bins within the cross correlation spectra, allowing (possible) calibration on a satellite (if the position of the satellite is known well enough…). When this argument is omitted, the astronomical calibration method for phasecal is used – astronomical methods assume a Gaussian spread within the cross correlation spectra and discard outliers (like satellites). In astronomical calibration the reported confidence interval (CI) is the CI of the mean angle estimate. In strong lock calibration the reported CI is the RMS angle fit across the band. There is generally no large penalty for using calstronglock on an astronomical calibration, other than that the astronomical mode provides improved CI estimates and slightly improved angle estimates.

--nodiag
Suppresses diagnostic sampling during observing. Provided as a courtesy function only, this option is never recommended.

--noatalo
Suppresses calls to the atasetskyfreq and atagetskyfreq commands. This is useful when running two beamformers on the same LO. The –f command must still be used (to convey the frequency to the beamformer software).
--corrsb [tiers] | --corrra [tiers]
Controls the data source for cross correlations in beamformer branch nodes. Give a comma separated list of tiers, where 0 is the top tier of the beamformer (ie, CP node) and successively higher numbers represent deeper tiers. Corrsb configures nodes on these tiers to correlate the input subbeam streams. Corrra configures nodes on these tiers to correlate the input reference antenna streams. This selection is sticky, and corrra is the default mode after startup for all nodes. As with reference antenna selection, the choice here selects the data that is passed to the next node in the tree (so corrsb will pass the reference subbeam in the refant stream).

--nocompress
Turns off data table compression. Data compression is on by default. The data compression function analyzes pointing information and stores only the most important information (for example, boundaries in discrete values). This switch should never be used unless debugging operation in which data compression is suspect. Improper use of this can cause the daemons to crash. This switch is not persistent, and is reset to use data compression on successive calls to bftrackephem.

--nofringe
Turn off the fringe rotators. If invoked, the fringe rotators will be disabled and only static delays and phases will be applied. Not recommended unless the application requires disabling fringe rotators. This switch is not persistent, and is reset to use the fringe rotators on successive calls to bftrackephem.

--conjfringe
Conjugates the fringe rotators. If invoked, the fringe rotators will be set to move opposite of the normal direction based on the fringe rate calculation. The conjugation of the starting phase is unaffected. This is a diagnostic switch only and used to debug the fringe rotators. Should not be used unless debugging new firmware. This switch is not persistent.

--specsrc [source]
Configures the source for the output spectrometers used with the –write out switch. Valid choices are “internal” and “external”. Selecting “internal” causes spectrometers in each beamformer to use their own data, which will always sample linear polarization. Selecting “external” causes spectrometers in each beamformer to use combined data from the downstream CP nodes, which is fed (post-combination) back upstream to the spectrometers. Default is “internal.” Use “external” when operating in circular polarization scenarios. This setting is persistent.

--tiergain [gain,tier]
Explicitly set the gain to the specified value across all FPGAs at the specified tier. The default gain is 2 and the maximum permitted value is
15. This is a linear voltage gain. Tier 0 is the CP node, with tier numbers increasing to deeper nodes (branch nodes have the highest tier value). This should only be used in cases where the –agc commands do not produce the desired results and manual gain setting is required.

Packetizer Arguments

--spk
Commands bftrackephem to update values in the SonATA packetizer daemons. Sets the sky frequency (when –freq is invoked) and polarization header (when –pol is invoked).

Example Implementations (*Older)
Example implementation #1:
obs@user1 | bbarott/bfu> | ./bftrackephem.rb | -f | 1420 | -d | 600 | -e
“/home/obs/bbarott/20080110/casa.ephem” | -n | 5 | --cal | –i | 10
--agcdb -6

To calibrate the beamformer over five iterations, using the current hookup (set by bfinit) with a skyfrequency of 1420 MHz, 10-second integration time for calibrations, and pre-loading 10 minutes of ephemeris data for the track from the given file for casa. The calibration will not take 10 minutes, but will only take as long as necessary for 5 iterations. The automatic gain controller will adjust the output beam level to be 6 dB below the “safe” level.

Example implementation #2:
obs@user1 | bbarott/bfu> | ./bftrackephem.rb | -f | 1420 | -d | 300 | -e
“/home/obs/bbarott/20080110/casa.ephem”

To cause the beam-former to track casa for five minutes at a sky frequency of 1420 MHz.

Example implementation #3:
obs@user1 | bbarott/bfu> | ./bftrackephem.rb | -f | 1420 | -d | 300 | -e
“/home/obs/bbarott/20080110/casa.ephem” --write “crosses” -i 5

To cause the beam-former to track casa for five minutes and record all cross-correlation results to a series of files.

Example implementation #4:
obs@user1 | bbarott/bfu> | ./bftrackephem.rb | -f | 1420 | -d | 3600 | -e
“/home/obs/bbarott/20080110/casa.ephem” --timer 5

To cause the beam-former to load an hour’s worth of tracking data for casa, and start the auto-update timer. Update control will be released to the BEEs rather than maintained in the user script.

Example implementation #5:
obs@user1 bbarott/bfu> ./bftrackephem.rb -f 1420 --azel 40.1,20.2 --timer 5 –d 300
To cause the beam-former to load five minute’s worth of data for a fixed azimuth and elevation, and start the timer for automatic updates.

Example implementation #6:
obs@user1 | bbarott/bfu> | ./bftrackephem.rb | -f | 1420 | --beamephem
x1,../ephem/casa.ephem,x2,../ephem/3c84.ephem –d 600
To cause the beam-former to load ten minute’s worth of data. All enabled antennas belonging to the “x1” beam (e.g., 1ax1, 1bx1) will be pointed to the ephemeris given by casa.ephem. All enabled antennas belonging to the “x2” beam (e.g. 1ax2, 1bx2) will be pointed to the ephemeris given by 3c84.ephem.

## Return Codes

The user scripts bftrackephem and bfinit use a uniform set of return codes. A return code of zero indicates successful operation. Any other return code asserts some alert condition. It is the user’s responsibility to interpret these codes. While most indicate failure (such as bad arguments and missing files), a few represent diagnostic conditions. Return codes below are given with their numeric and descriptive names. BeamOverflow and LinkError codes may be asserted with any other code or alone. Other codes cannot be asserted together.

BFERR_ExecOK | 0
BFERR_GeneralError | 1
BFERR_InternalError | 2
BFERR_DRbConnectionFailed | 11
BFERR_ExternalSystemCallFailed | 12
BFERR_InputError | 21
BFERR_MalformedArgument | 22
BFERR_BadAntennaList | 23
BFERR_BadInputFile | 24
BFERR_CalibrationOutOfScope | 41
BFERR_CalibrationFailed | 46
BFERR_BeamOverflow | 64
BFERR_LinkError | 128

## Software Daemons

The beamformer requires certain daemon processes to be active to function properly. A short description of these is below.

On Each BEE2: b01.bfa, b02.bfa… b05.bfa
A root-owned tree under /opt/bf/ contains subdirectories including:
/bin/ All ruby scripts go here. The daemon script exists here also. To stop daemons, run “./bfdaemon stop”, while to start them “./bfdaemon start”.
/bof/ All firmware files go here
/log/ Log files go here. Because the BEE2 file system is common, all bee2 log files can be accessed from any Bee2 machine.

On Boot2
A obs-owned tree under /opt/bfu/ contains subdirectories including:
/bin/ All ruby scripts go here. The daemon script exists here also. To stop daemons, run “./bfudaemon.rb stop”, while to start them “./bfudaemon.rb start”. This will control daemon processes for the Master, B01, B02… B05 servers. All daemons on the BEE2s must be running before these daemons can be successfully started. Daemons are titled “bxx_Beamformer_User_Server_bfa”, where xx is the BEE2 number (01 through 15), and “Master_Beamformer_User_Server_BFx” where x is the beamformer number 1..3.
/data/ All --write data is saved here, under a date/time stamped directory
/etc/ Configuration files go here, including hookups, antenna positions, and TDR estimates for fiber lengths.
/log/ Log files go here.

For the SonATA Packetizer
The SonATA packetizer also lives in /opt/bfu/bin. The daemon script “./spkdaemon start” and “./spkdaemon stop” controls the packetizer daemons. Daemons are titled “SonATA_Packetizer_Beamformer_Server_BFx” where x is the beamformer number 1..3.

## Indicator Lights

… Summary of indicator lights on BEE2s, iDACs, iADCs [in progress]

## A User’s Checklist

This guide may not be complete, but should serve as a good start-up for beamformer observations. See ATA documentation for more details about specific commands.

Make ready your ephemeris and ensure the telescopes are prepared for observing:
- ataephem [delay calibrator]
- ataephem [phase calibrator]
- ataephem [obs targets]
- atatrackephem [ant list] [delay calibrator]
- atasetpams [ant list]
- atasetfocus [ant list] [observing frequency] --cal
- atalnaon [ant list]

Initialize the beamfomer while waiting for the telescopes to track and focus to finish.
- bfinit –b [beamformer] –a [antpol list]
- bfibob sky
- bfibob walsh
- bfibob rearm

Check the focus, confirm settings for all antennas
- atagetfocus [antlist]

Repeat focus if any antennas report errors. Otherwise proceed setting for delay cal:
- atasetskyfreq c 1420
- bfibob autoatten
- bftrackephem –b [beamformer] –f 1420 –d [300] –i [15] –n
[4] –e [delay calibrator] –caldelay –agcdb -3

If delay calibration was good, proceed to obs. Frequency and calibrate
- atasetskyfreq c [obsfreq]
- bfibob autoatten
- atatrackephem [ant list] [phase calibrator]
- bftrackephem –b [beamformer] –f [obs freq] –d [i+200] – i[long time] –n[3] –e [phase calibrator] --calphase

Optionally but not required: Iterate the following for different offsets… 1 MHz, 10 MHz, 50 MHz, 100 MHz to refine your slope estimate. But whenever you do another phase cal, make sure it’s at the same obs freq (no offset).
- bftrackephem –b [beamformer] –f [obs freq + offset] –d [I+200] –I[long] –n[3] –e [phase calibrator] --calfreq

Just before observing, balance your inputs (Optional and potentially unstable)
- bftrackephem –b [beamformer] –f [obs freq] –d [30] –I[5] – n[3] –e [phase calibrator] –calamp

## Output file format

During observing, data is saved to time-stamped directories in a BFS file format. This is a tab-delimited format with one line per record. Each record is formatted as below:

% [0] Beamformer: | Indicates the beamformer ID (1 or 2 currently)
% [1] Data Type: | Category of write. See above.
% [2] Time (String): | String of current date/time (local time)
% [3] Time (Numeric): | Numeric (seconds since 1970), *not* atomic time (TAI)
% [4] Sky Frequency: | Floating point MHz
% [5] User Pointing: | The user's commanded ephemeris file, if present
% [6] User Offset Az: | The user's offset azimuth command
% [7] User Offset El: | The user's offset elevation command
% [8] Current Az: | The current azimuth (read from child ant?)
% [9] Current El: | The current elevation (read from child ant?)
% | Note az/el only work if pointing has been loaded
% | in this mode, and not as raw geopoint!
% [10] Hookup Type: | Category of hookup. (1) Antenna, (2) FPGA
% [11] Hookup Name: | String name of the hookup
% [12] CalDelay: | The bulk delay from the hookup cal
% [13] CalPhasorReal: | The phasor from the hookup cal, real part
% [14] CalPhasorImag: | The phasor from the hookup cal, imag part
% [15] CalDpDf: | The dp/df from the hookup cal
% [16] Obs time: | The observation time, in seconds
% [17] Data Length: | Reserved currently, but might be length of following data
% [18] idx: | The index number of the snap (optional)
% [19] pol: | The polarziation of the snap (optional)
% [20]..[24] | Reserved meta data
% [25…EOL] | Data pairs: R0, I0, R1, I1, R2, I2… etc.

## Programming Beam Calculators

The “Beam Calculator” is the fundamental object used to process pointing ephemeris (az/el versus time) into antenna-based geometric pointing tables (amplitude, phase, and delay). A versatile interface exists for creating and using custom beam calculators, as well as for providing arbitrary data to these calculators through bftrackephem. Additionally, it is possible to “debug” beam calculators without reinitializing the beamformer, greatly saving development time during testing.

By its nature, geoPoint data is purely geometric, and does not include calibration offsets. The programmer and user should not be concerned with amplitude and phase offsets, as they occur after the beam calculator stage and are hidden from view. However, the programmer should consider amplitude offsets, as it is probable that a calibration will result in unequal signal level among the antennas (eg, maximum SNR weighting). More details on this and the associated concerns will emerge when amplitude balancing has been fully implemented.

Before proceeding, there are a few ground rules:
1. The beamformer class BEAMCALCULATOR is defined at initialization, and contains information for basic pointing and also code to support user scripts.
2. User extensions should be self-contained files, and should extend the BEAMCALCULATOR class. These files are not in the beamformer home directories, but are pathed relative to bftrackephem.
3. User libraries may contain multiple pointing types. The file name determines the library name; the function name determines the pointing type.
4. When debugged, new beam calculators can be deployed to the main library. See Billy Barott to get these approved for the official release code.
5. The phase-center of the beam is defined with the --ephem command. Other ephemeris (such as null positions) should be loaded with –bcephem.
6. Beam groups, as will be discussed, represent a single beam processor and are designated by the polarization and unique beam id (e.g. “x1” or “y1”). However, there is little need for the developer to be aware of different beam groups, as each one receives a copy of the beam calculator and is effectively independent.

Objects accessible from the Beam Calculator
The beam calculator functions may access the following objects:

The following class variables are accessible by the user-defined beam-calculator. However, extreme caution is recommended if you decide to use these directly, as the support code has been designed to eliminate the need for such direct access.

@vars
A Hash list containing variable data. Preferred method of accessing is with getClassVariable(), although direct access is allowed.

@beamtype
The type of beam specified with –bctype (string). This is automatically interpreted, so the user should not need to access this.

@antenna
A complete Hash list of all antennas in the beam former. Again, the user should not access this unless there is an overwhelming reason. Use the list provided by enabledAntennasInGroup() instead.

@bgname
A string containing the descriptive name of the current beamgroup (e.g., “x1” or “y1”

@bglist
An array containing string hash names of all antennas within the current beam group (even disabled ones). This should not need to be accessed by the user.

The following methods are accessible by the user-defined beam-calculator, and are recommended in common use:

enabledAntennasInGroup()
Returns an array whose elements are each ANTENNAHOOKUP objects. Each element of the array is guaranteed to be a member of the current beam group, and also to be enabled in the current hookup. The preferred method of calculating coefficients is to iterate through this group.

getClassVariable(varname, erronempty = true) The preferred method of access for local variables. Varname is a string containing the name of the variable as the user should have loaded it with –bcvar. The erronempty flag determines whether the function will raise on error to the operating system if a nil value is encountered (indicating that no value was loaded by the user). This is recommended true for required data that can take on no default value in your code (or, when so important that you wish to alert the user to a possible mis-spelling of the variable name). This is recommended false for optional variables, or variable lists (for example, when iterating through null0, null1, null2, null3… until a nil value is encountered).

calculateTimeLimits(t0in, tmaxin, ephem) Determines the temporal bounds to use in calculating data tables. This is best to invoke in the standard way seen in the demo code.
Sample Code
The source code on the following pages represents some demonstrations of beam calculator classes. The first is the code that is included for the default beam, beamDefaultPhased. The second is for a simple projection nulling algorithm.

Note that the variable name “ephemeris” is reserved.

def beamDefaultPhased(interpolationInterval, t0in = nil, tmaxin = nil) #==============================================================
# Generates a simple phased on-axis beam

# First, generate a list of antennas that we'll be working with.

# Note that ephemeris should be loaded as VALUEARRAYs: A data holder # with azimuth and elevation coded vs time entries.

# Even for fixed pointing, we should use the VALUEARRAY: It supports # the .interpolate() method for fixed pointings and is a more general # application than having fixed arrays. #==============================================================

ants = enabledAntennasInGroup() | # An object list
ephem = @vars["ephemeris"] | # The current ephemeris

# Get the first and last points in the ephemeris, as loaded by the user # and filter as requested by the just-in-time limits.

# This will establish the range of times for interpolation.

t0, tmax = calculateTimeLimits(t0in, tmaxin, ephem)

# Clear all currently existing geometric pointing data from

# all enabled antennas. This is required before new data can be # added to the data tables.

ants.each{|ant|
ant.clearGeoPoint()
}

#==================================================================== # The preceeding lines are setup for calculating the beam. The

# following lines do the actual calculation. Note that we must

# iterate forward through time, because geoPoint data must be loaded

# forward-chronologically. #====================================================================

# Now, step-interpolate through all times that were valid in the ephem: t0.step(tmax, interpolationInterval) { |tai|

# The following lines extract ephemeris data for the current time. # From a value array, data is in the format: [tai, [az, el]] currentEphemItem = (ephem.interpolate(tai))

currentTAI = currentEphemItem[0]
currentAzelPair = currentEphemItem[1]
currentAz = currentAzelPair[0]
currentEl = currentAzelPair[1]

# For every antenna that's currently enabled in this group: ants.each{|ant|

# Return an ordered triple of the geometric

# pointing correction required for this az/el.

# The antenna object computes these corrections based on # its individual antenna position.

rc = ant.geometricPointing(currentAz, currentEl)

# Below is delay correction to be applied, in samples currentSampleDelay = rc[0]

# Below is the amplitude weighting (pre-cal), and should # “always” be returned as 1.

currentFringeAmplitude = rc[1]

# Below is the fringe phase at the current pointing,

# in unwrapped radians (range is NOT zero to 2 PI). The

# user should never wrap this phase to zero/2PI, because it # is used to calculate fringe rate.

currentFringePhase = rc[2]

# Now that we've calculated the required correction

# offsets for this antenna at this time, we write this

# data back to the current antenna. Alternatively, we

# could manipulate this data further (e.g. dither the phase # or process the array manifold through a projection null). # Note that this data does NOT include calibration offsets # of any sort: Those are added automatically by the

# beamformer at a later stage.

currentGeoPoint = [currentTAI, [currentSampleDelay, currentFringeAmplitude, currentFringePhase]] ant.addGeoPoint(currentGeoPoint)
}
}
end

Notice that there is really very little code in the above example. This code should make an excellent starting point for additional algorithms, and one more is included on the next page. Note that the following example is shown as an entire file, as the user might create.

#============================================================== # This code has not been revised for just-in-time beamforming # See previous example for t0, tmax assignments and proper

# arguments into beam calculator functions. #============================================================== ############################################################### #

# engbeamcalc1.rb

# Contains some demonstration code for beam nulling. # Specifically, this extends the beam calculator with:

# | beamAxialNull()

# | --> VAR = "nullorder"

# | --> Ephem = "ephemeris" (default ephemeris only)

# Author: William C. Barott

# Original Date: July 26, 2008

# Last Revised Date:

class BEAMCALCULATOR
#=============================================================== # This is an extension to the BEAMCALCULATOR. When ruby loads # this file, it will reopen the BEAMCALCULATOR class and add

# this additional functionality. Comments from the standard beam # calculator have been omitted to save space. #===============================================================

def beamAxialNull(interpolationInterval)
# Generates a simple null beam.

ants = enabledAntennasInGroup() | # An object list
ephem = @vars["ephemeris"] | # The current ephemeris

nullorder = (getClassVariable("nullorder", true)).to_i
nants = ants.length | # Total number of ants
# The null order determines how many "cycles" we will distribute # our antennas around. EG, null order 1, we will dither phases # around the unit circle "once." (so for 4 antennas, we get phases # of 0 90 180 270, or null order 2 at each of 0, 180.

t0 = ((ephem.getData(0)).getData)[0]
tmax = ((ephem.getData(ephem.length - 1)).getData)[0]

# Clear current data.

ants.each{|ant|
ant.clearGeoPoint()
}

t0.step(tmax, interpolationInterval) { |tai| currentEphemItem = (ephem.interpolate(tai)) currentTAI = currentEphemItem[0] currentAzelPair = currentEphemItem[1] currentAz = currentAzelPair[0]
currentEl = currentAzelPair[1]

ants.each_index{|antidx|
ant = ants[antidx]
rc = ant.geometricPointing(currentAz, currentEl) currentSampleDelay = rc[0]

currentFringeAmplitude = rc[1] currentFringePhase = rc[2]

# Now alter the fringe phase to create a null: alteredFringePhase = currentFringePhase + (antidx.to_f / nants) * 2 * PI * nullorder

# We're going to write the altered fringe phase

# to create the null we just made. currentGeoPoint = [currentTAI, [currentSampleDelay, currentFringeAmplitude, alteredFringePhase]] ant.addGeoPoint(currentGeoPoint)

}
}
end

end

## Selected Documentation for Beamformer Objects

The following pages contain selected documentation on the VALUEARRAY and ANTENNAHOOKUP classes. These have been limited to the methods that users might find to be of interest when programming their own beam calculators.

## Class VALUEARRAY (selected methods)

new(parent, mode, norder, dsize)object parent, string mode, integer norder, integer dsize
Creates a new VALUEARRAY object and returns it to the environment. Parent and mode are reserved for other functions of the VALUEARRAY not exposed here. It is permissible to set them both to nil, although they must be included arguments.

Norder and dsize determine the dimensions of the underlying data of which the VALUEARRAY is comprised. Norder is the differential order (number of Taylor expansion terms), and at present should always be set to 1. dsize is the number of discrete values that the array will handle. So, for example, azimuth and elevation coordinates are handled by a valuearray with norder = 1 and dsize = 2.

getData(idx) | integer idx → VALUEHOLDER
Returns the VALUEHOLDER at the given index.
getDataArray() | → array of VALUEHOLDER
Returns a pointer to the entire data array of VALUEHOLDERS.
length() | → integer
Returns the length of the data array held by the VALUEARRAY. Functionally the same as myobject.getDataArray().length()
addData(indata) | array indata
Adds a row of data to the VALUEHOLDER array. This data should be entered in the required format, generically [T, [X0, X1, X2], [X0’, X1’, X2’]]. For example, azel pointing is added [tai, [az, el]]. Note that the new data must occur at a later time than data already in the tables, otherwise interpolation will break.

clearData()
Removes all data from the VALUEHOLDER array, resetting it to an empty array.
trimOldData(tai) | float tai
Removes all data from the data array where the time index is before the time included in the argument. Saves “one-point-before” the threshold for maintaining valid interpolation.

interpolate(tai) | float tai → array
Returns an array of data in the standard format, e.g. [T, [X0, X1, X2], [X0’, X1’, X2]]. The “T” should be the same as the TAI argument. Each data point results from a linear interpolation of the temporally nearest entries in the data table.

## Class ANTENNAHOOKUP (selected methods)

getHashName()
Returns the antenna’s unique hash name, for example 3gx1 is the hash name for antenna 3g, x-polarization, first copy. Note that x1 is also the beam group name.
getTSys(optional freq) | float freq → float
Returns the noise temperature for the antenna. If freq is included, calculates at the given frequency. If freq is omitted, calculates at the current sky frequency. Note that TSys values are not guaranteed to be absolute, but ratios between antennas should be correct.
getATAID() | → string
Returns the ATA ID node and antenna, for example 1a.
getATAPol() | → string
Returns the polarization, x or y, for the current antenna.
addAzEl(indata) | array indata
Adds an entry to the azimuth / elevation data table for this antenna. Input data must be of the standard format as an array: [tai, [az, el]]. Data must be entered sequentially, such that every entry is “after” the last entry chronologically. An error will occur during interpolation if this condition is not satisfied.

Note that this data table is used strictly for meta-pointing information. It is preloaded with ephemeris as specified by the user’s –ephem command. However, the savvy programmer might wish to alter this meta table if the new beam calculator changes the primary pointing substantially from the “ephemeris.”

setAzEl(indata) | array indata
Clears the az/el data table for this antenna and writes one entry, the indata. The same rules as addAzEl apply.

clearAzEl()
Clears the az/el data table.
getAzEl(tai) | float tai → array

Commands the azel data table to interpolate, returning the pointing at a given time. The pointing data is returned in the format [az,el]. The method should return [0,0] if an error occurs accessing the table.

addGeoPoint(indata) | array indata
Adds an entry to the geometric pointing database. This data indicates the applied correction to the antenna and conform to [tai, [delay, amp, phase]]. The same rules apply as for other data tables. The delay is in units of full-samples (but can have a fractional part). Amplitudes must not exceed 1 (clipping). Phase is in unwrapped radians (e.g. not constrained to –pi/pi) to facilitate fringe rotation.
setGeoPoint(indata) | array indata
Replaces the geometric pointing database with the given data.

clearGeoPoint()
Clears the geometric pointing table, leaving it empty.
geometricPointing(az,el) | float az, float el → array
Solves the current antenna’s geometric pointing data for the given azimuth and elevation. Returns corrections of delay (in samples), phase (in unwrapped radians), and amplitude that, when applied to this antenna, would cause the data to re-reference to the origin of the coordinate system. Calibration information is not included in this data, as calibration is applied after the beam-calculator. Data is returned in the format Please note the following:
1. Data represents corrections required to phase the given antenna with the coordinate origin, not the response of an antenna to the stimulus. The currently assigned sky frequency is taken into account.
2. Phases are unwrapped, meaning that they are continuous and not constrained to the –pi/pi range. It is important that the user maintain continuous phase when reassigning phases to the antennas. This is because the fringe rotator differentiates these phases, and will encounter problems if phases are discontinuous.

## Other Matters

Sometimes things take a minute. If they seem to take an abnormally long time, you might try resetting the daemons. If you do this on boot2 before stopping your script, you’ll sometimes get more diagnostic information when the daemons stop than you would have gotten otherwise.

If something appears broken, please contact me and we’ll get it resolved.

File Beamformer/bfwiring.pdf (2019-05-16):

# Beamformer Wiring (Beamformer #1): X-Polarization BEE2 Cascade (Beam Proc #1)

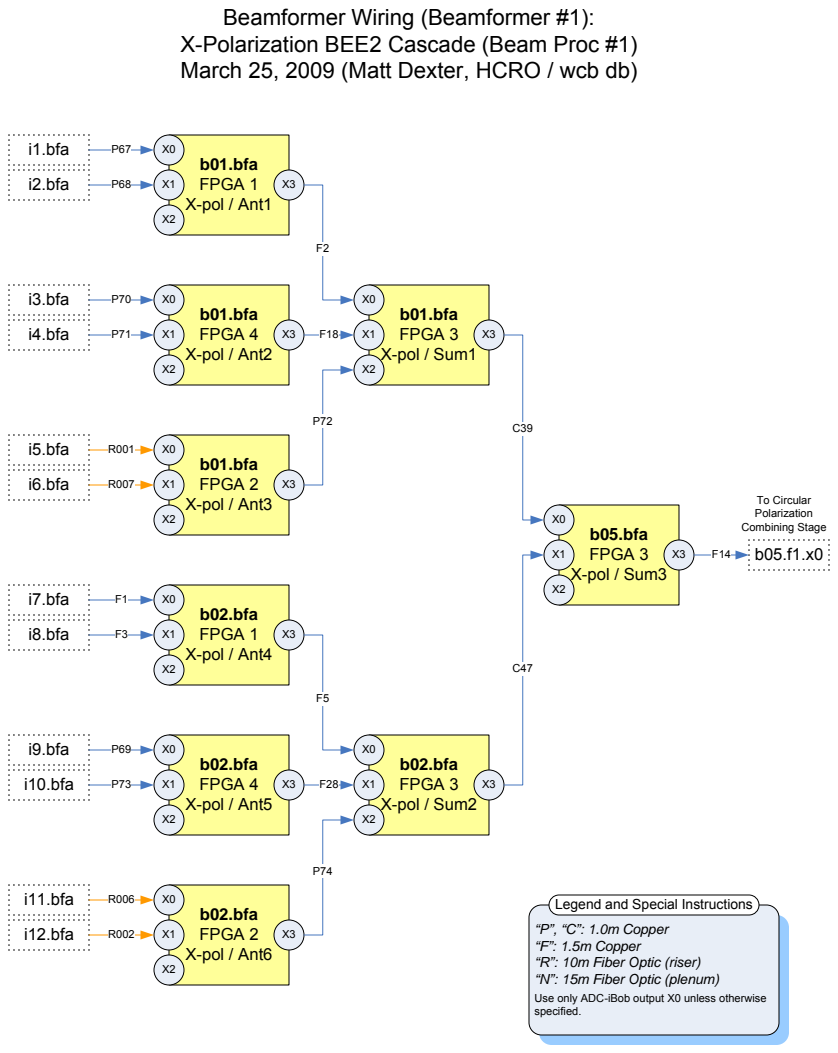
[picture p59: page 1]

March 25, 2009 (Matt Dexter, HCRO / wcb db)

Legend and Special Instructions
“P”, “C”: 1.0m Copper
“F”: 1.5m Copper
“R”: 10m Fiber Optic (riser)
“N”: 15m Fiber Optic (plenum)
Use only ADC-iBob output X0 unless otherwise
specified.

## b03.bfa FPGA 1

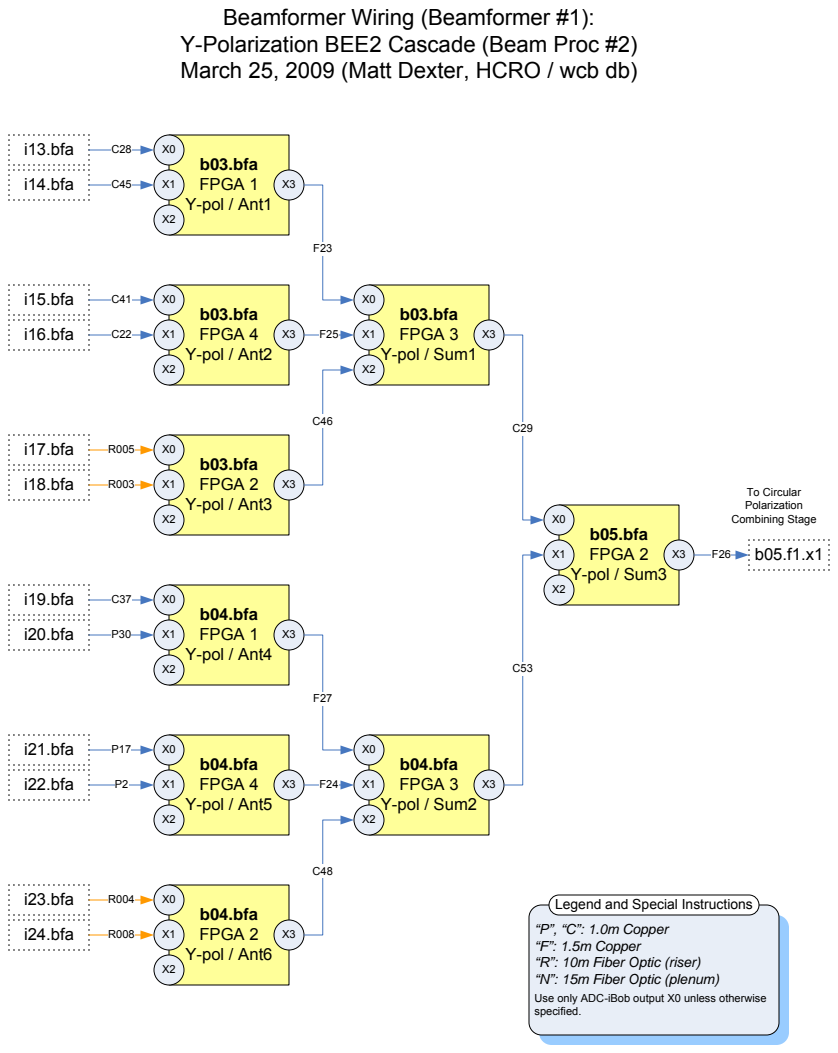
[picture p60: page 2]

Beamformer Wiring (Beamformer #1):
Y-Polarization BEE2 Cascade (Beam Proc #2)
March 25, 2009 (Matt Dexter, HCRO / wcb db)

Legend and Special Instructions
“P”, “C”: 1.0m Copper
“F”: 1.5m Copper
“R”: 10m Fiber Optic (riser)
“N”: 15m Fiber Optic (plenum)
Use only ADC-iBob output X0 unless otherwise

## b06.bfa FPGA 1

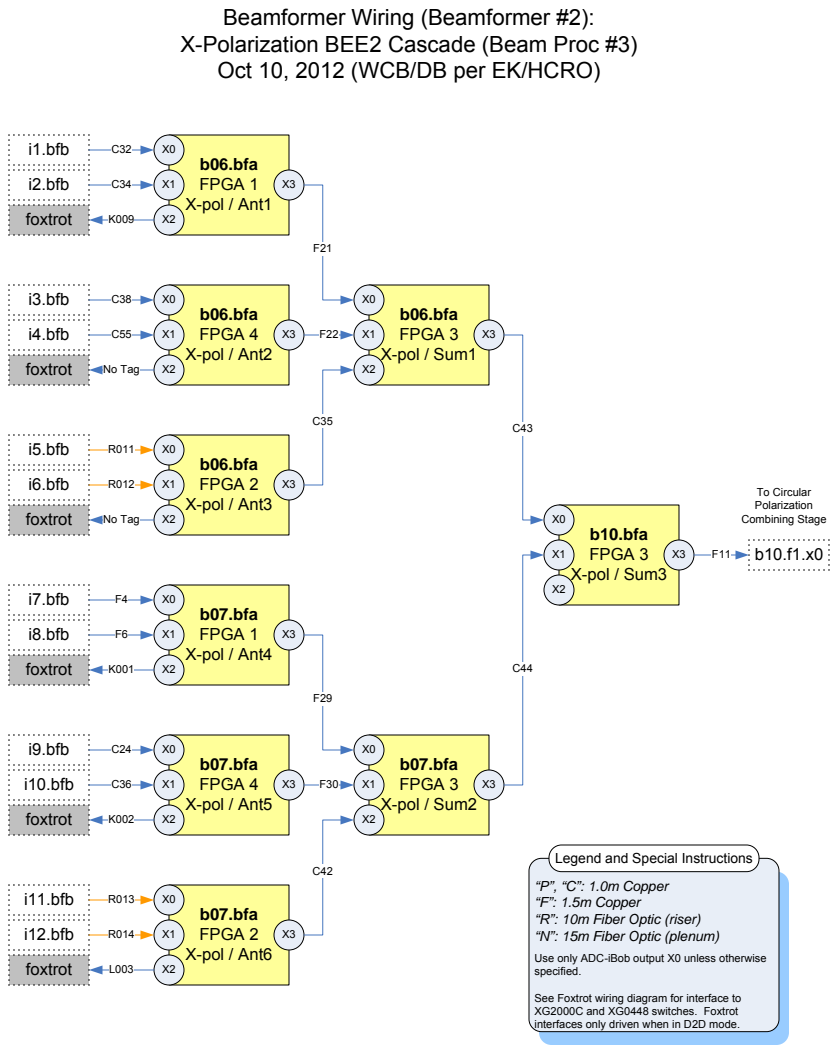
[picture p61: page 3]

Beamformer Wiring (Beamformer #2):
X-Polarization BEE2 Cascade (Beam Proc #3)
Oct 10, 2012 (WCB/DB per EK/HCRO)

Legend and Special Instructions
“P”, “C”: 1.0m Copper
“F”: 1.5m Copper
“R”: 10m Fiber Optic (riser)
“N”: 15m Fiber Optic (plenum)
Use only ADC-iBob output X0 unless otherwise
specified.

See Foxtrot wiring diagram for interface to
XG2000C and XG0448 switches. Foxtrot
interfaces only driven when in D2D mode.

## b08.bfa FPGA 1

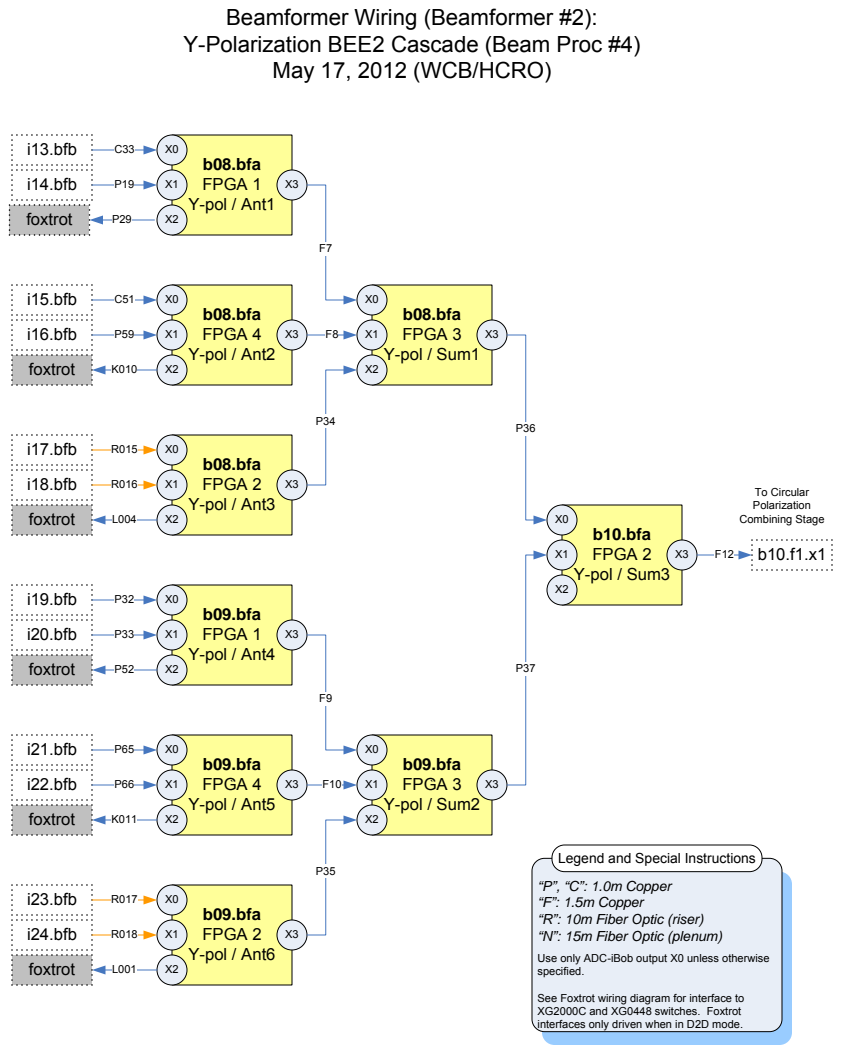
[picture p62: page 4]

Beamformer Wiring (Beamformer #2):
Y-Polarization BEE2 Cascade (Beam Proc #4)

Legend and Special Instructions
“P”, “C”: 1.0m Copper
“F”: 1.5m Copper
“R”: 10m Fiber Optic (riser)
“N”: 15m Fiber Optic (plenum)
Use only ADC-iBob output X0 unless otherwise
specified.

See Foxtrot wiring diagram for interface to
XG2000C and XG0448 switches. Foxtrot
interfaces only driven when in D2D mode.

# Beamformer Wiring (Beamformer #3): X-Polarization BEE2 Cascade (Beam Proc #5)

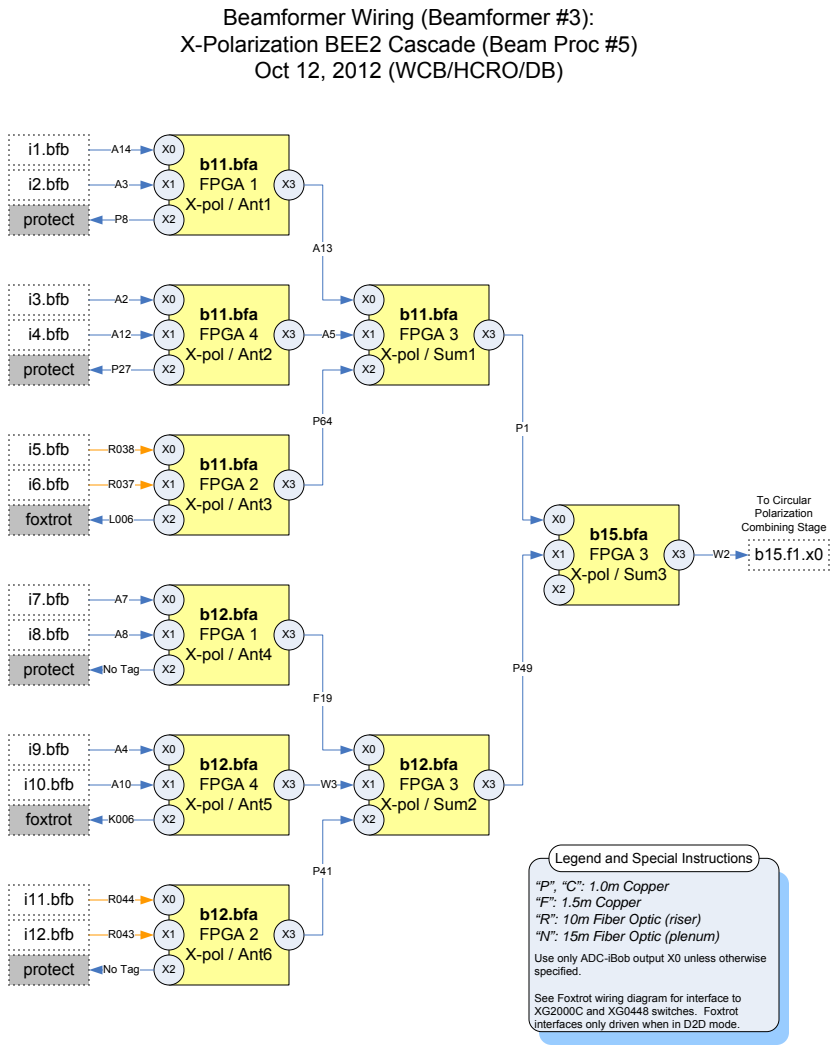
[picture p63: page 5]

Oct 12, 2012 (WCB/HCRO/DB)

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

See Foxtrot wiring diagram for interface to
XG2000C and XG0448 switches. Foxtrot
interfaces only driven when in D2D mode.

## b13.bfa FPGA 1

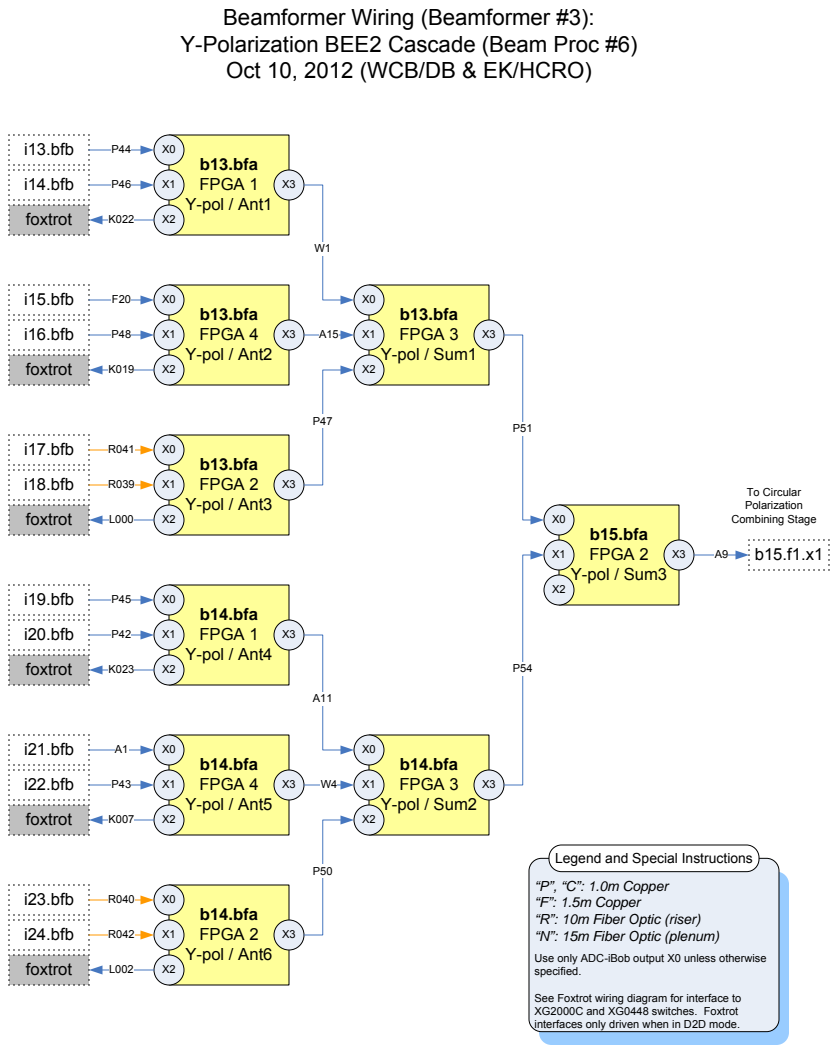
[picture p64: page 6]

Beamformer Wiring (Beamformer #3):
Y-Polarization BEE2 Cascade (Beam Proc #6)
Oct 10, 2012 (WCB/DB & EK/HCRO)

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

## b05.f3.x3

## b05.f2.x3

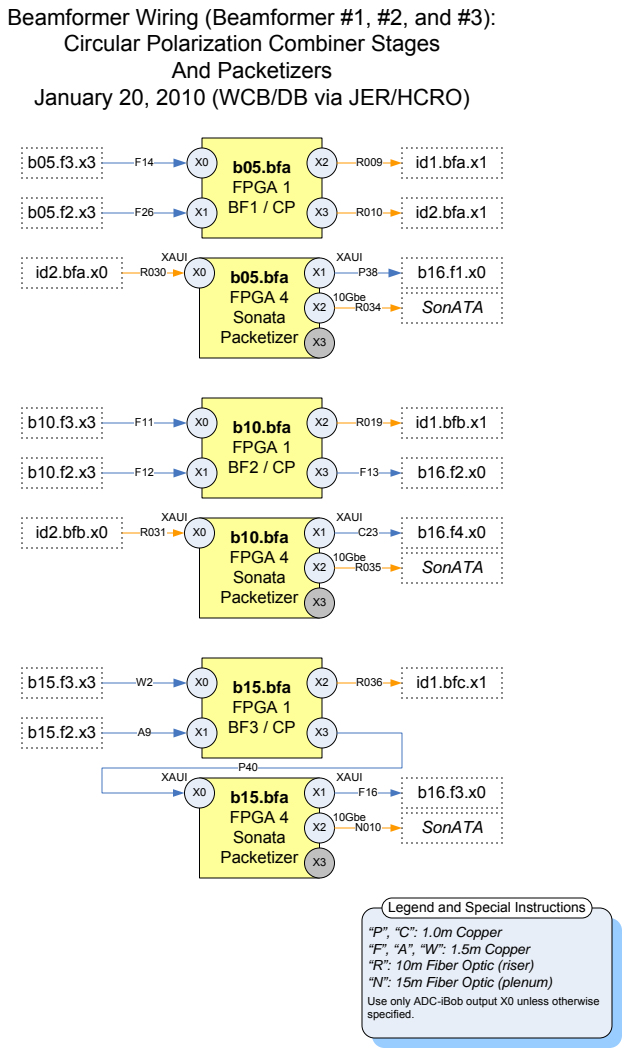
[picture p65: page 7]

Beamformer Wiring (Beamformer #1, #2, and #3):
Circular Polarization Combiner Stages

January 20, 2010 (WCB/DB via JER/HCRO)

Legend and Special Instructions
“P”, “C”: 1.0m Copper
“F”, “A”, “W”: 1.5m Copper
“R”: 10m Fiber Optic (riser)
“N”: 15m Fiber Optic (plenum)
Use only ADC-iBob output X0 unless otherwise

## id1.bfa XR-Pol

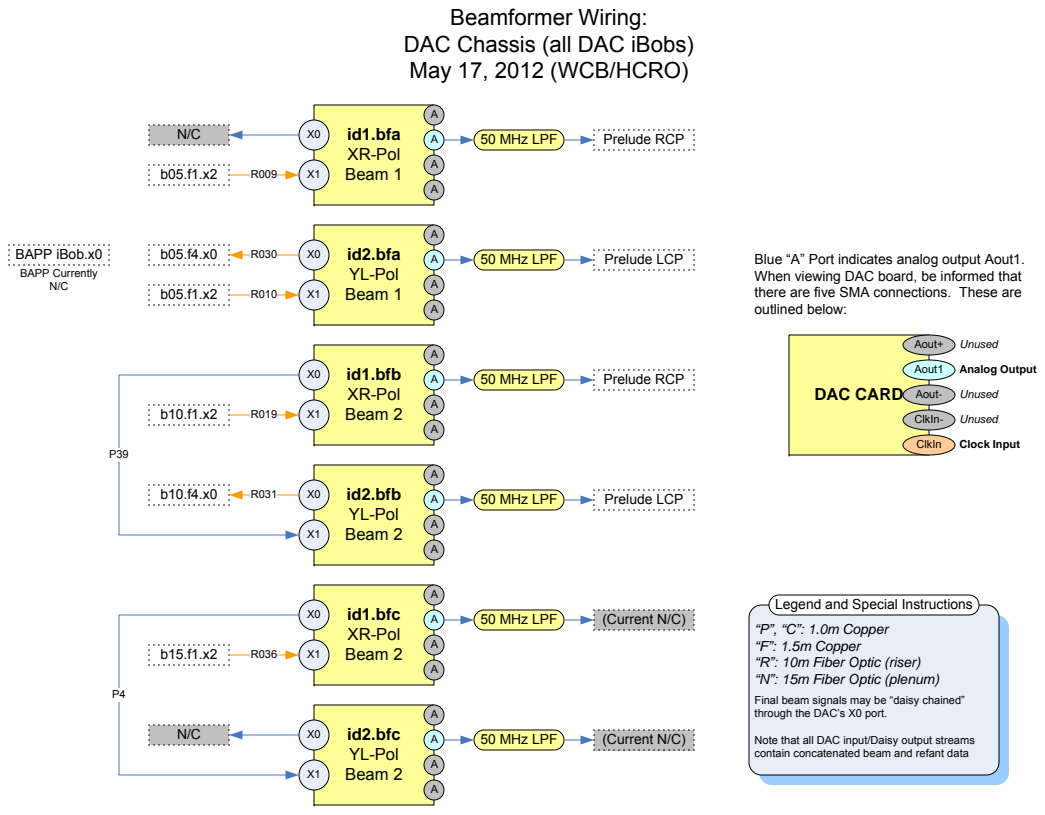
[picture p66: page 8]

Beamformer Wiring:
DAC Chassis (all DAC iBobs)
May 17, 2012 (WCB/HCRO)

Blue “A” Port indicates analog output Aout1.
When viewing DAC board, be informed that
there are five SMA connections. These are
outlined below:

Legend and Special Instructions
“P”, “C”: 1.0m Copper
“F”: 1.5m Copper
“R”: 10m Fiber Optic (riser)
“N”: 15m Fiber Optic (plenum)
Final beam signals may be “daisy chained”
through the DAC’s X0 port.

Note that all DAC input/Daisy output streams
contain concatenated beam and refant data

# Beamformer Wiring – Auxiliary Processor (B16) May 17, 2012 (WCB/HCRO)

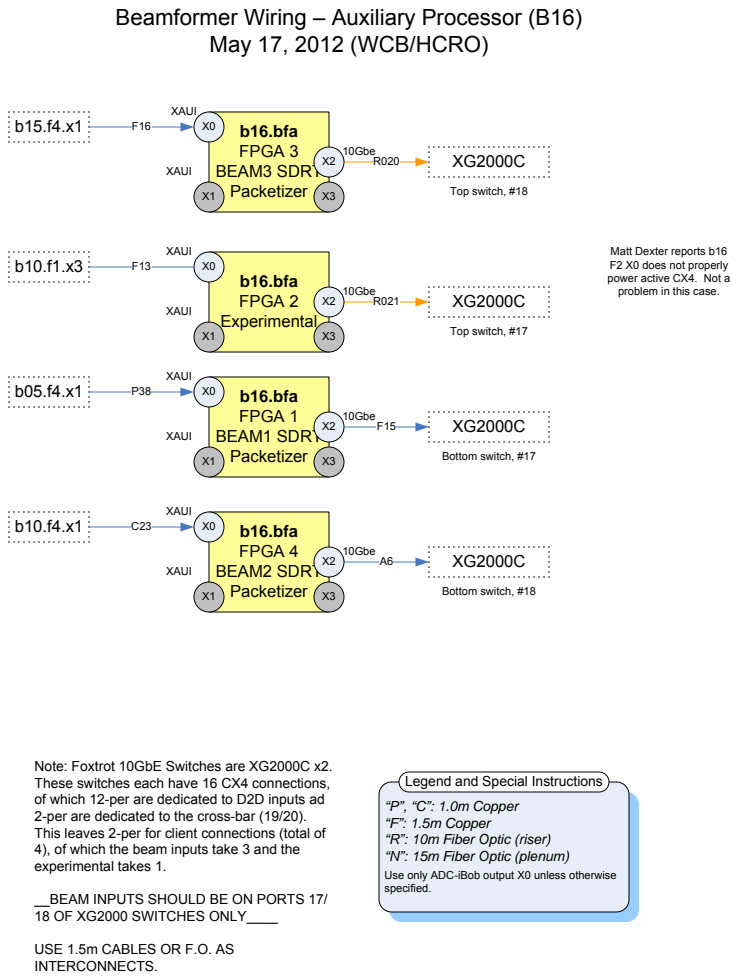
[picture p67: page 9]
XAUI; b16.bfa FPGA 2 Experimental; 10Gbe; b16.bfa FPGA 1 BEAM1 SDRT Packetizer; b16.bfa FPGA 4 BEAM2 SDRT Packetizer; b16.bfa FPGA 3 BEAM3 SDRT Packetizer; Bottom switch, #18; Bottom switch, #17; Top switch, #17; Top switch, #18

Matt Dexter reports b16
F2 X0 does not properly
power active CX4. Not a
problem in this case.

Note: Foxtrot 10GbE Switches are XG2000C x2.
These switches each have 16 CX4 connections,
of which 12-per are dedicated to D2D inputs ad
2-per are dedicated to the cross-bar (19/20).
This leaves 2-per for client connections (total of
4), of which the beam inputs take 3 and the
experimental takes 1.

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

__BEAM INPUTS SHOULD BE ON PORTS 17/
18 OF XG2000 SWITCHES ONLY____

USE 1.5m CABLES OR F.O. AS
INTERCONNECTS.

# Beamformer Wiring (BF#1): Top Chassis iBobs (i1 – i8)

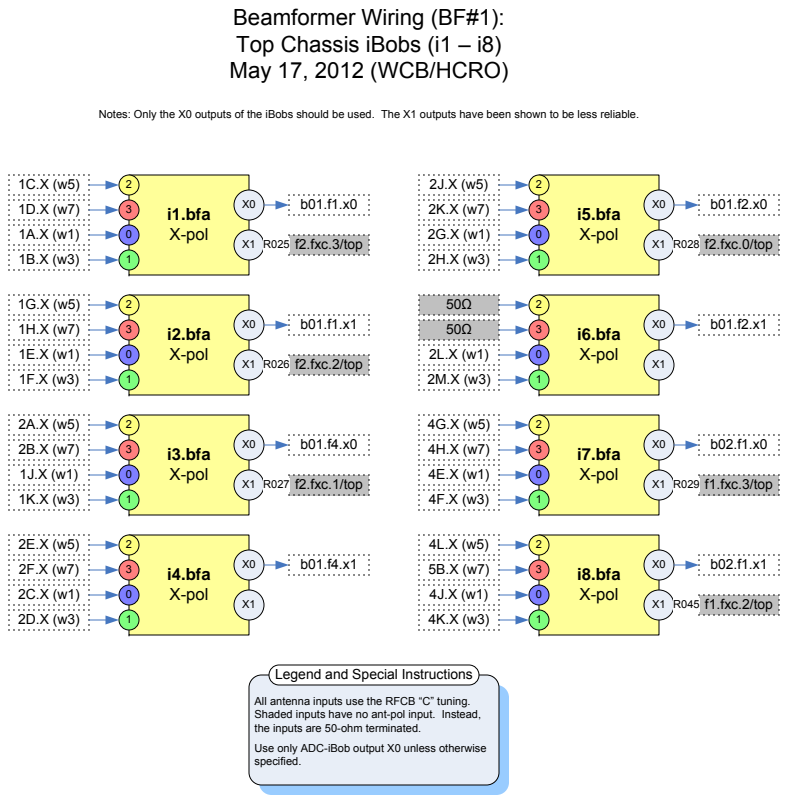
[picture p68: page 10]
i1.bfa X-pol; i2.bfa X-pol; i3.bfa X-pol; i5.bfa X-pol; i4.bfa X-pol; i8.bfa; X-pol; i7.bfa X-pol; i6.bfa X-pol; f2.fxc.3/top; f2.fxc.2/top; f2.fxc.1/top; f2.fxc.0/top; f1.fxc.3/top; f1.fxc.2/top

May 17, 2012 (WCB/HCRO)

Notes: Only the X0 outputs of the iBobs should be used. The X1 outputs have been shown to be less reliable.

Legend and Special Instructions

All antenna inputs use the RFCB “C” tuning.
Shaded inputs have no ant-pol input. Instead,
the inputs are 50-ohm terminated.
Use only ADC-iBob output X0 unless otherwise

# Beamformer Wiring (BF#1): Middle Chassis iBobs (i9 – i16)

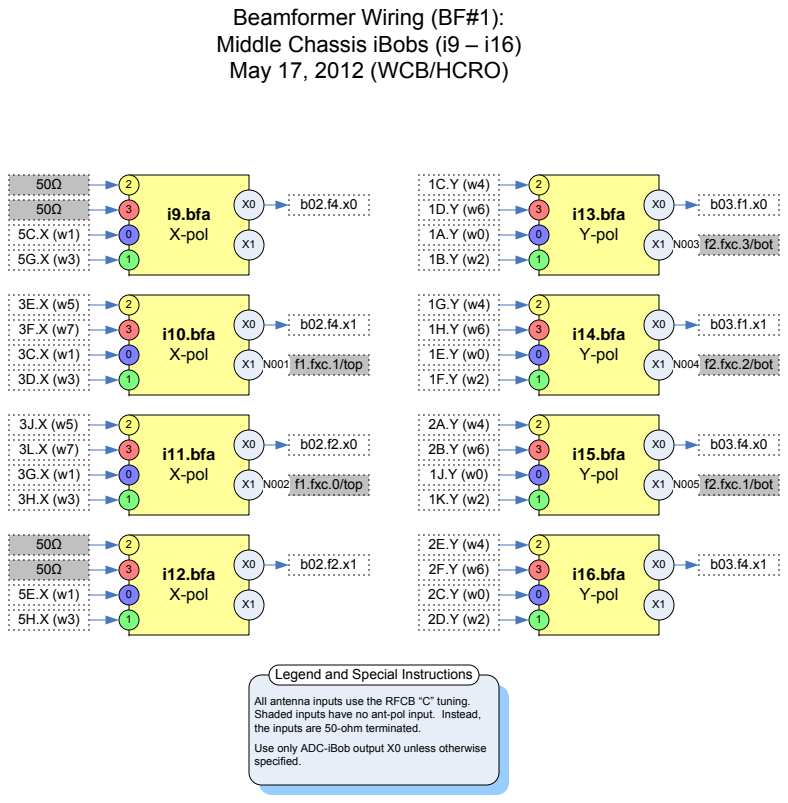
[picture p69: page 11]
i9.bfa X-pol; i10.bfa X-pol; i12.bfa X-pol; i13.bfa Y-pol; i14.bfa Y-pol; i15.bfa Y-pol; i16.bfa Y-pol; i11.bfa X-pol; f1.fxc.1/top; f1.fxc.0/top; f2.fxc.3/bot; f2.fxc.2/bot; f2.fxc.1/bot

May 17, 2012 (WCB/HCRO)

Legend and Special Instructions

All antenna inputs use the RFCB “C” tuning.
Shaded inputs have no ant-pol input. Instead,
the inputs are 50-ohm terminated.
Use only ADC-iBob output X0 unless otherwise

# Beamformer Wiring (BF#1): Bottom Chassis iBobs (i17 – i24)

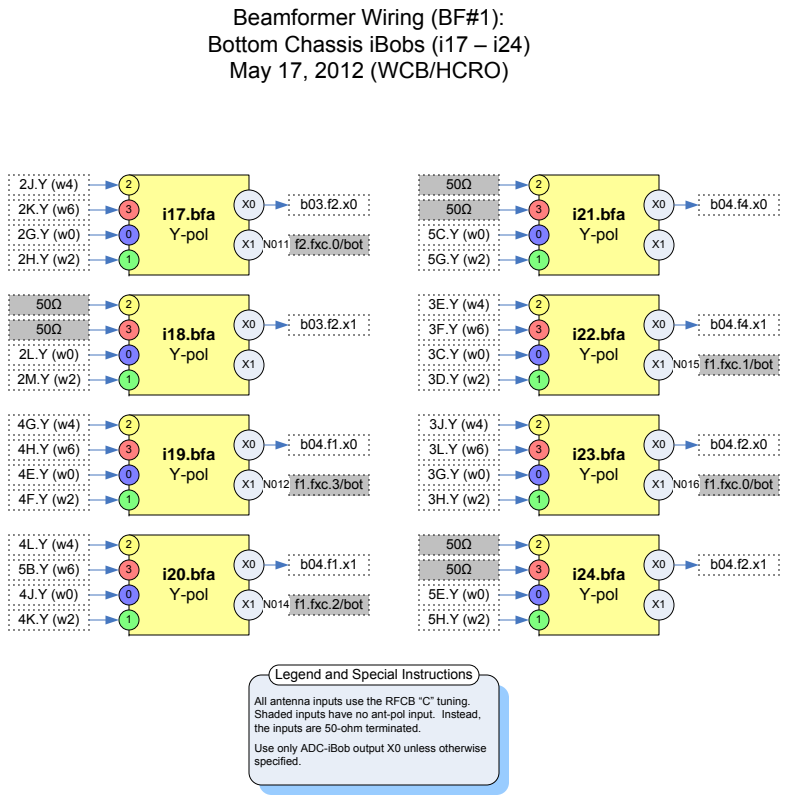
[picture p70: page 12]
i17.bfa Y-pol; i18.bfa Y-pol; i19.bfa Y-pol; i20.bfa Y-pol; i21.bfa Y-pol; i22.bfa Y-pol; i23.bfa Y-pol; i24.bfa Y-pol; f2.fxc.0/bot; f1.fxc.3/bot; f1.fxc.2/bot; f1.fxc.1/bot; f1.fxc.0/bot

May 17, 2012 (WCB/HCRO)

Legend and Special Instructions

All antenna inputs use the RFCB “C” tuning.
Shaded inputs have no ant-pol input. Instead,
the inputs are 50-ohm terminated.
Use only ADC-iBob output X0 unless otherwise

# Beamformer Wiring (BF#2): Top Chassis iBobs (i1 – i8)

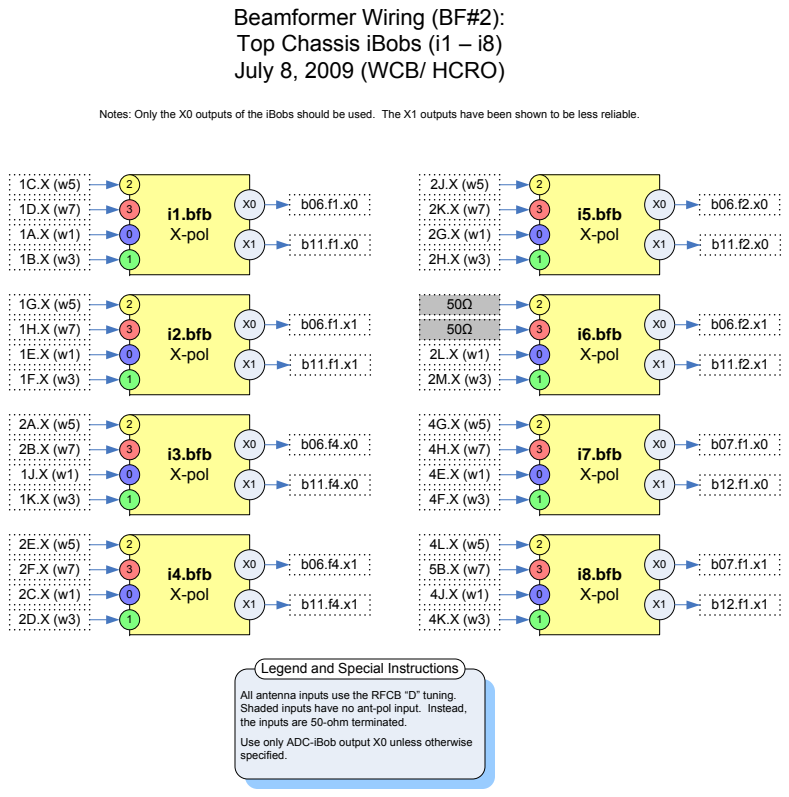
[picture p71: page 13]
i1.bfb X-pol; i2.bfb X-pol; i3.bfb X-pol; i5.bfb X-pol; i4.bfb X-pol; i8.bfb; X-pol; i7.bfb X-pol; i6.bfb X-pol

July 8, 2009 (WCB/ HCRO)

Notes: Only the X0 outputs of the iBobs should be used. The X1 outputs have been shown to be less reliable.

Legend and Special Instructions

All antenna inputs use the RFCB “D” tuning.
Shaded inputs have no ant-pol input. Instead,
the inputs are 50-ohm terminated.
Use only ADC-iBob output X0 unless otherwise

# Beamformer Wiring (BF#2): Middle Chassis iBobs (i9 – i16)

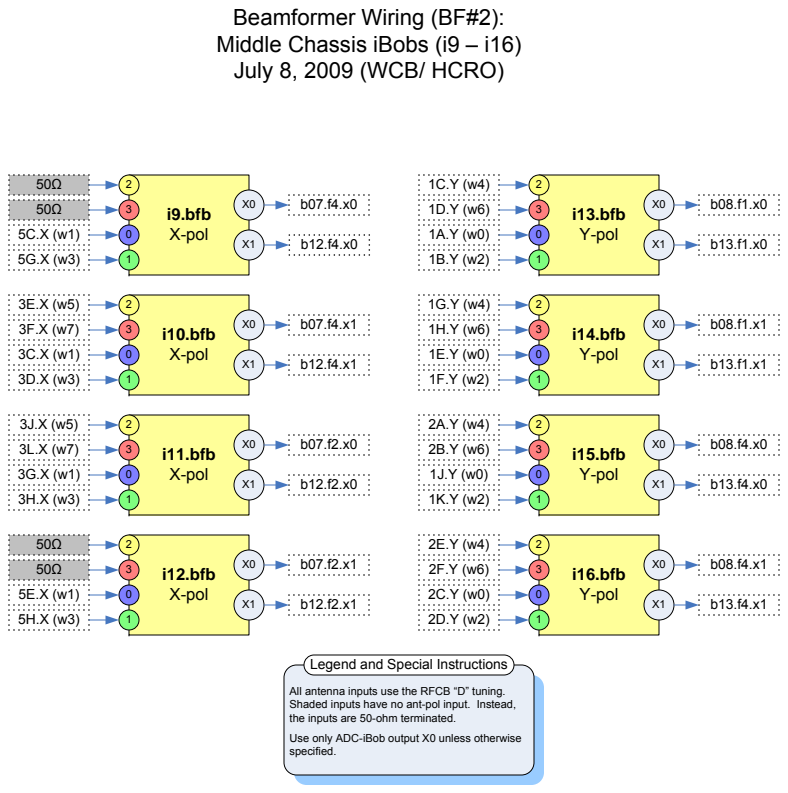
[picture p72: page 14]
i9.bfb X-pol; i10.bfb X-pol; i12.bfb X-pol; i13.bfb Y-pol; i14.bfb Y-pol; i15.bfb Y-pol; i16.bfb Y-pol; i11.bfb X-pol

July 8, 2009 (WCB/ HCRO)

Legend and Special Instructions

All antenna inputs use the RFCB “D” tuning.
Shaded inputs have no ant-pol input. Instead,
the inputs are 50-ohm terminated.
Use only ADC-iBob output X0 unless otherwise

# Beamformer Wiring (BF#2): Bottom Chassis iBobs (i17 – i24)

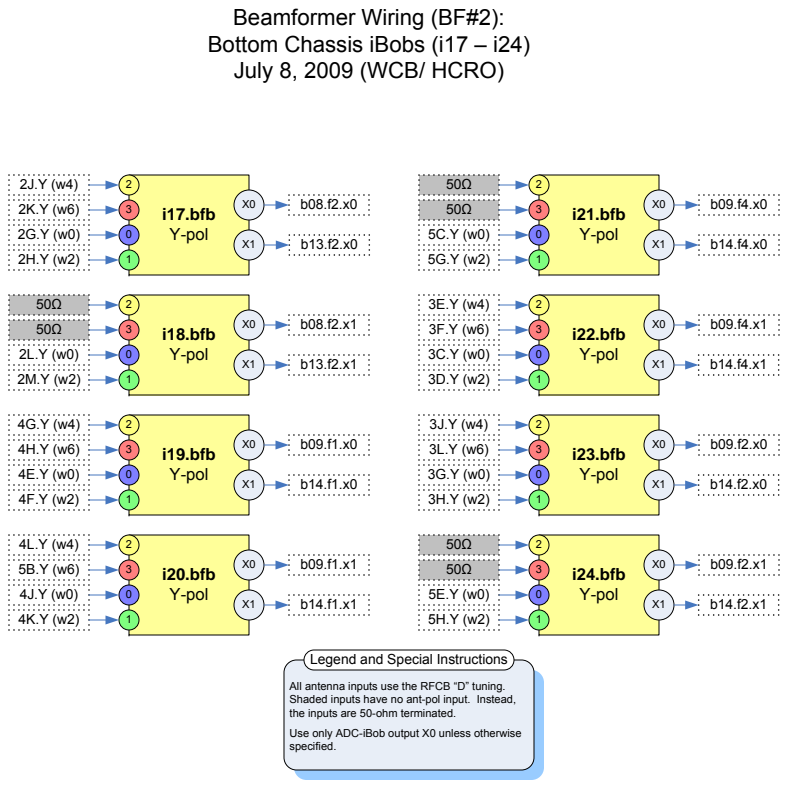
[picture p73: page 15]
i17.bfb Y-pol; i18.bfb Y-pol; i19.bfb Y-pol; i20.bfb Y-pol; i21.bfb Y-pol; i22.bfb Y-pol; i23.bfb Y-pol; i24.bfb Y-pol

July 8, 2009 (WCB/ HCRO)

Legend and Special Instructions

All antenna inputs use the RFCB “D” tuning.
Shaded inputs have no ant-pol input. Instead,
the inputs are 50-ohm terminated.
Use only ADC-iBob output X0 unless otherwise

# Beamformer Wiring (10GbE Backbone to Foxtrot-Quito) Beamformer #3 Rack May 17, 2012 (WCB/HCRO)

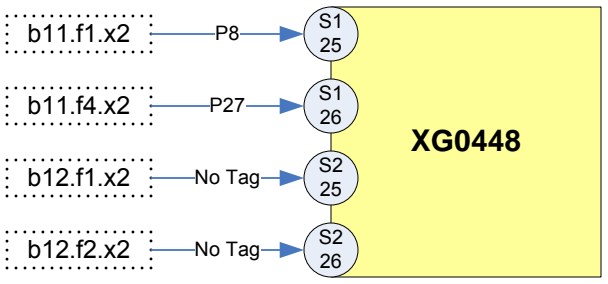
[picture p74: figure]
No Tag

# Beamformer Wiring: BEE2 FPGA Physical Layout July 28, 2008: WCB / HCRO

FPGA #1 | FPGA #4
FPGA #2 | FPGA #3

## Front View of the BEE2 (Fiber-side)

X-2 | X-0 | X-1 | X-3 | X-1 | X-3 | X-2 | X-0
FPGA #1 | FPGA #4 C-Flash
X-2 | X-0 | X-1 | X-3 | X-0 | X-1 | X-1 | X-3 | X-2 | X-0
FPGA #3 | FPGA #2
Ethernet

## Back View of the BEE2 (Analog IF side)

2 | 0 | 1 | 3

## Center FPGA

1 | 3 | 2 | 0
0 | 2 | 3 | 1 | 1 | 0 | 3 | 1 | 0 | 2

## Top View of the BEE2

## Analog IF Analog Fiber

C.Flash

Net

X-2 | X-0 | X-1 | X-3 | X-0 | X-1 | X-1 | X-3 | X-2 | X-0
FPGA #3 | FPGA #2
Ethernet

## Expanded Back View of the BEE2 (Analog IF side)

RS232

RS232

DVI

SW/

Fuse

User
Clock
SMA

DVI

### b01.bfa b02.bfa b03.bfa b04.bfa b05.bfa

### Fan Tray

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
### Fan Tray

### (Blank)

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
### Fan Tray

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
## Rack Layout Front (Analog IF) View

### Ethernet Switch

### b10.bfa

### b06.bfa b07.bfa b08.bfa b09.bfa

### Fan Tray

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
### Fan Tray

### (Blank)

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
### Fan Tray

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
### Ethernet Switch

### b16.bfa

### b11.bfa b12.bfa b13.bfa b14.bfa

### Fan Tray

### id1.bfa

### id2.bfa

### id1.bfb

### id2.bfb

### BAPP / Procurve Switch

### b15.bfa

### Outflow

## Beamformer #1 Tuning C

## Beamformer #2 Tuning D Auxiliary Processor B16

## Beamformer #3 Tuning D DAC Outputs

### id1.bfc

### id2.bfc

### XG2000C / Foxtrot Switch

### XG2000C / Foxtrot Switch

### XG0448 / Foxtrot-Quito Switch

# Beamformer Rack Layout Front (Analog RF) View May 17, 2012 (WCB/HCRO)

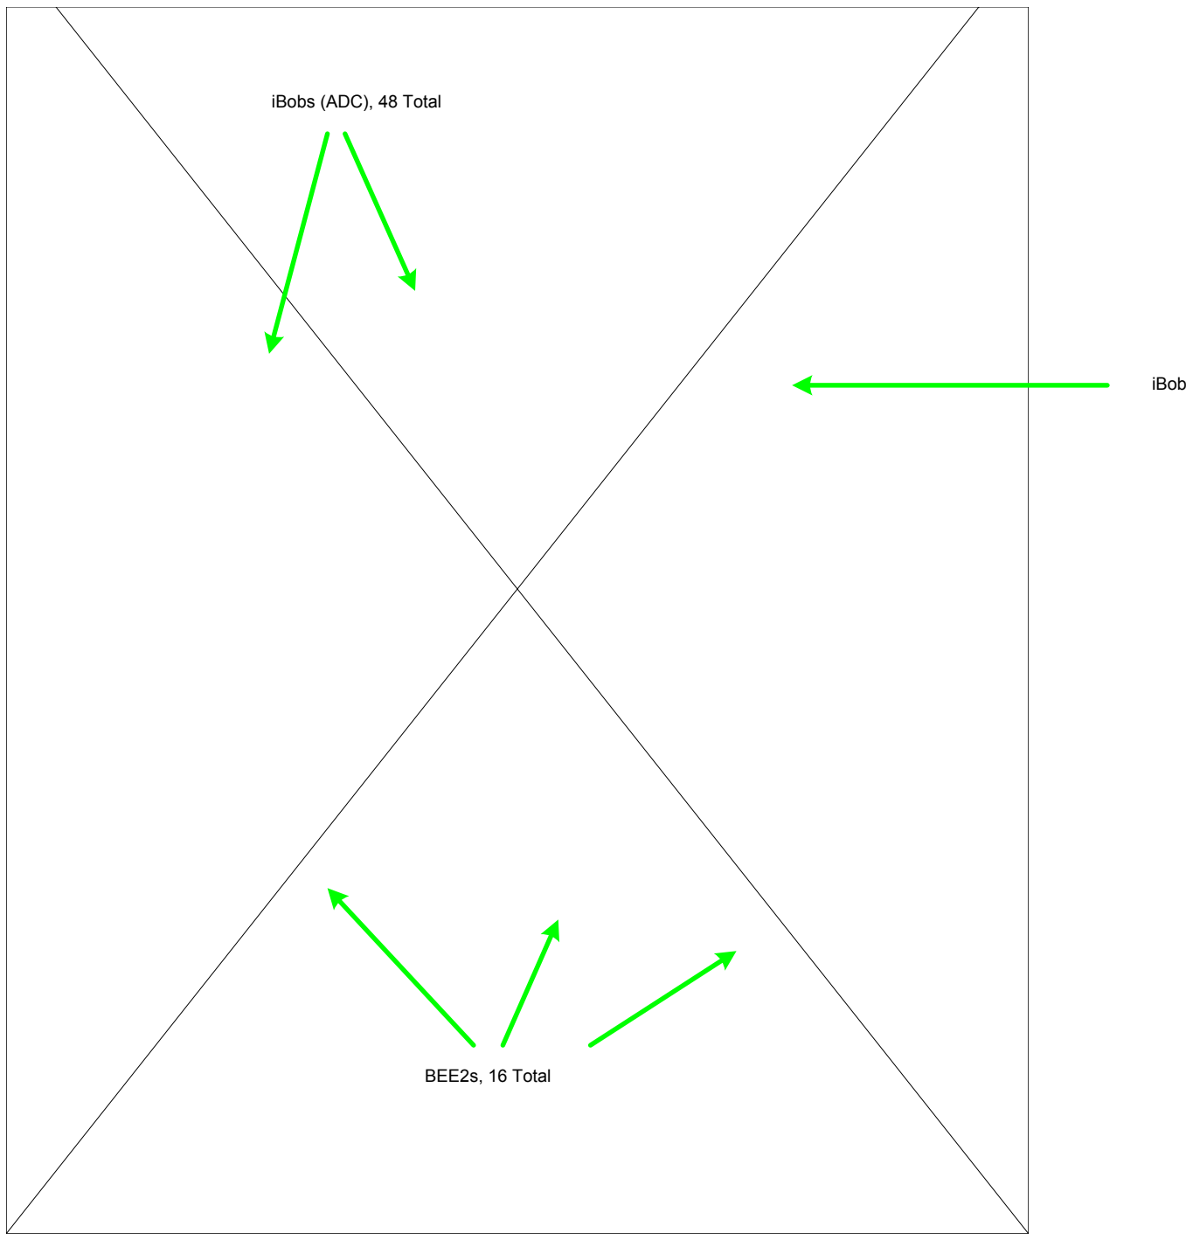
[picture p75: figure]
iBobs (ADC), 48 Total; iBob; BEE2s, 16 Total

## XG2000C Switches

# Beamformer Wiring:

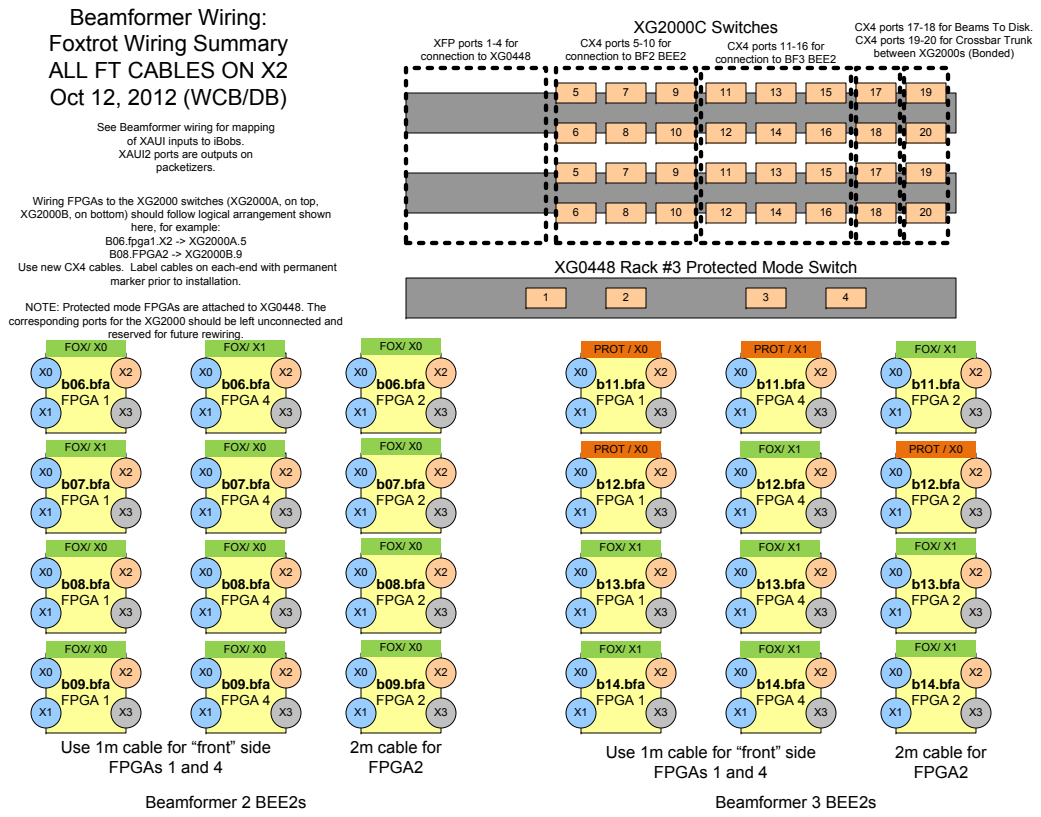
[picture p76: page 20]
b11.bfa FPGA 1; b12.bfa FPGA 1; b13.bfa FPGA 1; b14.bfa FPGA 1; b11.bfa FPGA 4; b12.bfa FPGA 4; b13.bfa FPGA 4; b14.bfa FPGA 4; b11.bfa FPGA 2; b12.bfa FPGA 2; b13.bfa FPGA 2; b14.bfa FPGA 2; b06.bfa FPGA 1; b07.bfa FPGA 1; b08.bfa FPGA 1; b06.bfa FPGA 4; b07.bfa FPGA 4; b08.bfa FPGA 4; b09.bfa FPGA 4; b06.bfa FPGA 2; b07.bfa FPGA 2; b08.bfa FPGA 2; b09.bfa FPGA 2; 2m cable for FPGA2; Beamformer 3 BEE2s; CX4 ports 5-10 for connection to BF2 BEE2; CX4 ports 11-16 for connection to BF3 BEE2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

CX4 ports 17-18 for Beams To Disk.
CX4 ports 19-20 for Crossbar Trunk
between XG2000s (Bonded)

Foxtrot Wiring Summary
ALL FT CABLES ON X2
Oct 12, 2012 (WCB/DB)

XFP ports 1-4 for
connection to XG0448

See Beamformer wiring for mapping
of XAUI inputs to iBobs.
XAUI2 ports are outputs on
packetizers.

Wiring FPGAs to the XG2000 switches (XG2000A, on top,
XG2000B, on bottom) should follow logical arrangement shown

XG0448 Rack #3 Protected Mode Switch

Use new CX4 cables. Label cables on each-end with permanent

marker prior to installation.

NOTE: Protected mode FPGAs are attached to XG0448. The
corresponding ports for the XG2000 should be left unconnected and

reserved for future rewiring.

b09.bfa
FPGA 1
Use 1m cable for “front” side
FPGAs 1 and 4
Beamformer 2 BEE2s

## Bee#1 FPGA 1

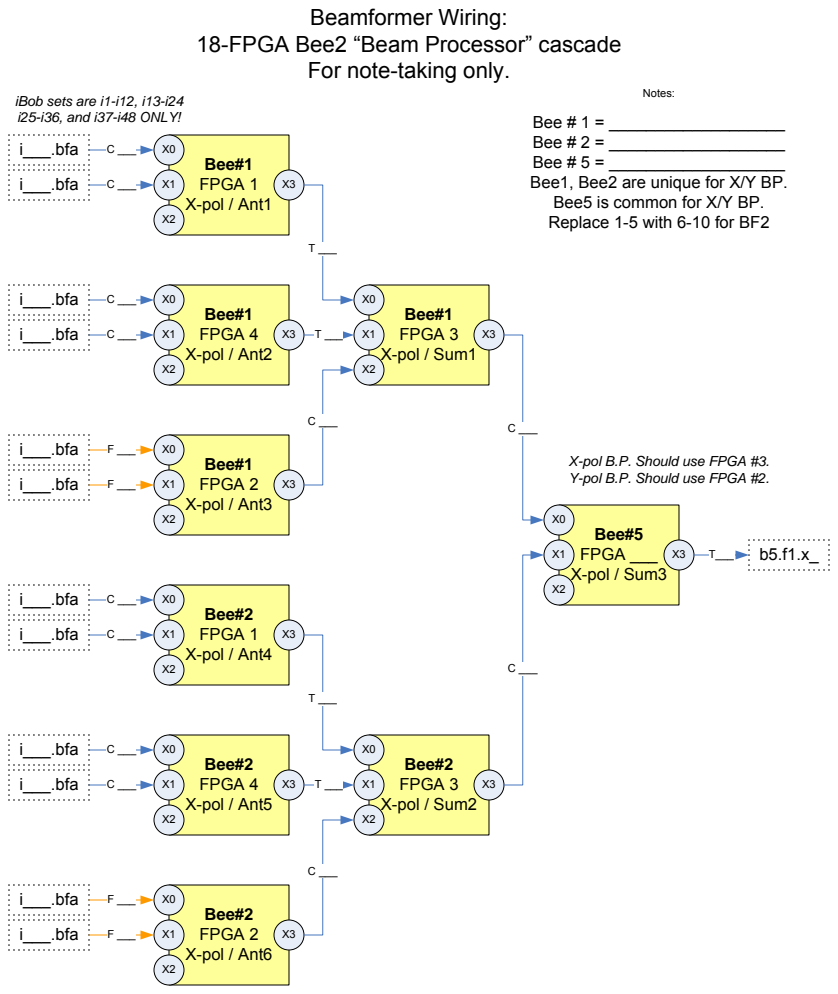
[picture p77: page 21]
X-pol / Ant1; Bee#1 FPGA 4 X-pol / Ant2; Bee#1 FPGA 2 X-pol / Ant3; Bee#2 FPGA 1 X-pol / Ant4; Bee#2 FPGA 4 X-pol / Ant5; Bee#2 FPGA 2 X-pol / Ant6; Bee#1 FPGA 3 X-pol / Sum1; Bee#2 FPGA 3 X-pol / Sum2; Bee#5 FPGA ___ X-pol / Sum3; Beamformer Wiring:; i___.bfa; Notes:

18-FPGA Bee2 “Beam Processor” cascade

For note-taking only.

iBob sets are i1-i12, i13-i24
i25-i36, and i37-i48 ONLY!
i___.bfa

Bee # 1 = ___________________
Bee # 2 = ___________________
Bee # 5 = ___________________
Bee1, Bee2 are unique for X/Y BP.
Bee5 is common for X/Y BP.
Replace 1-5 with 6-10 for BF2

X-pol B.P. Should use FPGA #3.
Y-pol B.P. Should use FPGA #2.

# Beamformer Wiring (Beamformer #1 and #2): Circular Polarization Combiner Stages For rewiring (PLANNING ONLY)

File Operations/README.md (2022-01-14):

Link to ATA Operations Spreadsheet (based on brainstorming slides in this directory): 

https://docs.google.com/spreadsheets/d/1ybRrEYc5dTBGziV-v7WsL5tUnEioAHx_giK-miuFgpI/edit?usp=sharing

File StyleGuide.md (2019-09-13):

# HCRO STYLEGUIDE

## Python

Since python is widely used at the HCRO, SETI, and academia in general, this will be the most fleshed-out style guide.

You must adhear to the [PEP8 Style Guide](https://www.python.org/dev/peps/pep-0008/) with only a few deviations.

### Linting

> TLDR; running `pylint` on your files should have a score >= 9 

Lint your code with [pylint](https://www.pylint.org/). Install pylint with:
```
$ pip install pylint
```
And run it on your file with:
```
$ pylint myscript.py
```
Unless you are a statistical anomaly, this will show you dozens or hundreds or warnings and fixes along with a score. As a basic rule of thumb, **any score >= 9.0 passes** muster. If you find these warnings to be a little too pedantic, there are several things you can add to your config file `~/.pylintrc`.
* disable=invalid-name  This will allow you to use variable names like `ra` and `el` but use them sparingly.
* Want to disable the warnings about tabs? Too bad, don't.

### Keepin' it Stylish   
There is a great auto-linter called [autopep8](https://pypi.org/project/autopep8/), a script that will fix all the little things it can. This will take care of the majority of the linters warnings with one command.

Install with:

```
$ pip install autopep8
```

And run the script with:

```
$ autopep8 --in-place --aggressive --aggressive myscript.py
```

Or if there's no chance in hell youll remember that, try adding an alias like so:

```
$ echo "alias mylint='autopep8 --in-place --aggressive'" >> ~/.bash_profile
$ source  ~/.bash_profile
$ mylint myscript.py
```

//TODO add section on git-hooks?

### Note to Scientists 

A few pices of advice for those not trained in programming:

* Complexity is unavoidable but complicated code is optional. Try to avoid uniformly procedural programming which is programming where the execution runs through the program line by line (like how a jupyter notebook works). General advice is to write a class or function, make damn sure it works, then forget about it. This will make your programs readable and will help debugging. If you can reduce frustration while debugging, it will help you, your blood pressure, your relationships, the list goes on...
* It is much better to be over descriptive than under descriptive. Laziness isn't an excuse with modern text editors and IDEs which have auto-complete. `time_in_ms_since_jan_1970` is preferable to `t` although `time_utc` is probably ideal in this situation.
* The Python dictionary is the king of data types, know how to use them and your programs will be simpler and faster.

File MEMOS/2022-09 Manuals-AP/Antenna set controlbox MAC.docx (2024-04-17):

# This document describes how to set the MAC address in the DHCP server at control.hcro.org after a controlbox swap.

## Intro:

Connect to control as ROOT “ssh root@control”

nano /etc/dhcp/dhcpd.ataants.conf

systemctl restart isc-dhcp-server.service

## Important:

To check what is on the antenna network run:

arp -i ens2f3

Dr. Alexander Pollak | SETI INSTITUTE | alexander.pollak.87@gmail.com

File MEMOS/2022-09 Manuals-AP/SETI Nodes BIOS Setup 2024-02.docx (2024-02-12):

# This document describes the Bios settings for the SETI Nodes at HCRO

## Intro:

Settings are based on the current configuration of SETI-node4 and the GPU server setup from COSMIC. : https://github.com/COSMIC-SETI/FrontPage/blob/master/Nodes/GPU-Compute/Setup.md

## Adjust BIOS for HPC:

Boot Setup:

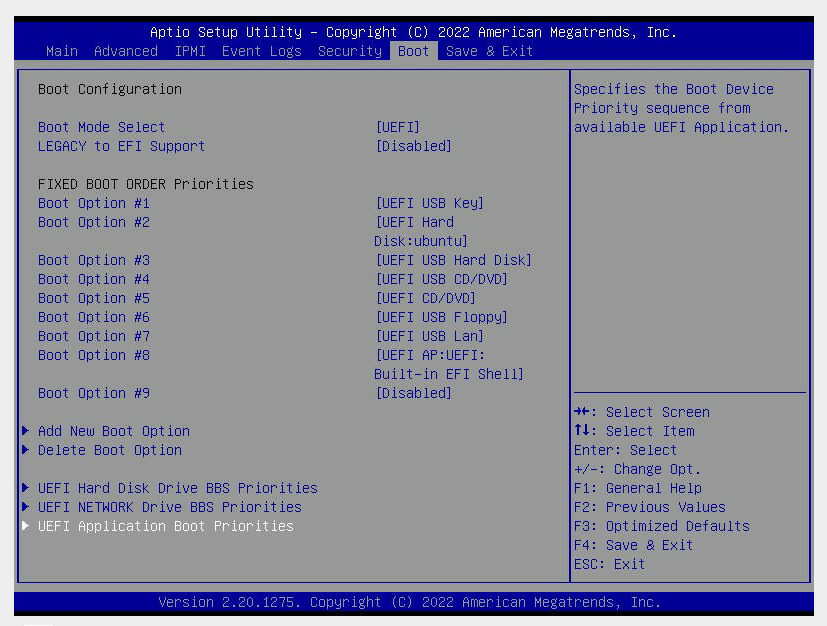
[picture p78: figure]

Boot Feature:

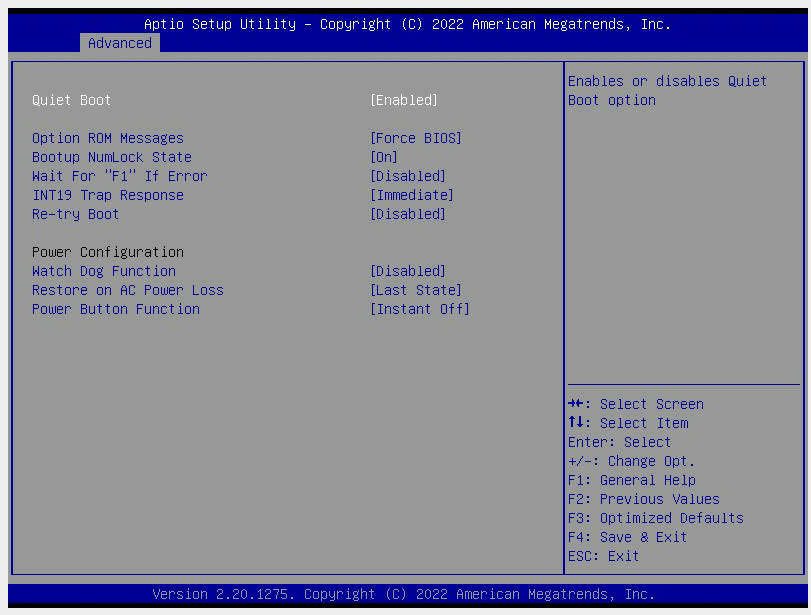
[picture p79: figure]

CPU Configuration:

- SMT = disabled [CPU Configuration]
- SVM Mode = disabled [CPU Configuration]
- Local APIC mode = x2APIC [CPU Configuration]

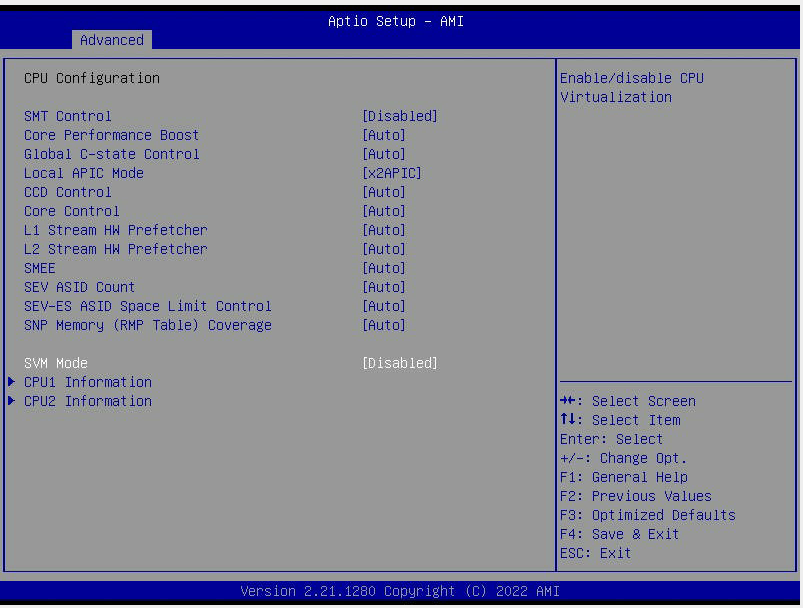
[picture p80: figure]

NB Configuration:

- APBDIS = 1 [NB Configuration]
- Fixed SOC Pstate = P0 [NB Configuration]
- IOMMU = disabled [NB Configuration]
- DF Cstates = disabled [NB Configuration]

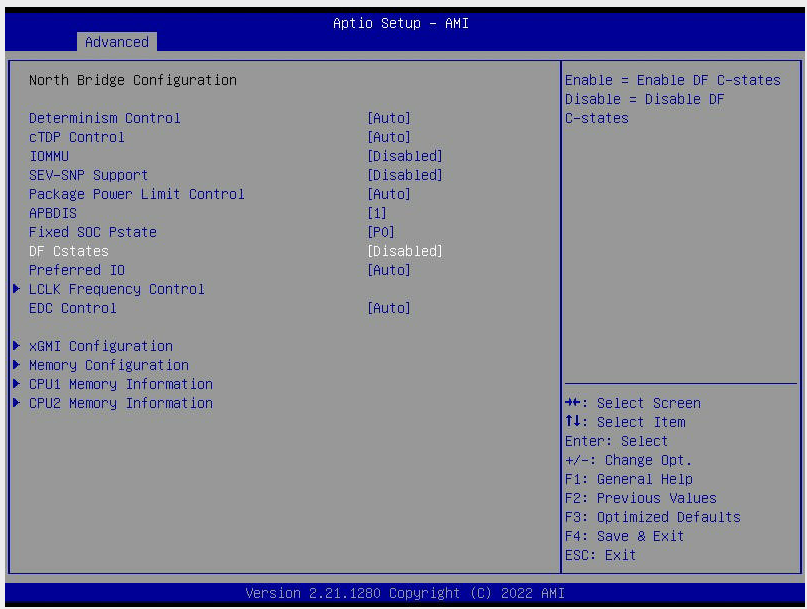
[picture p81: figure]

ACPI Configuration:

- NUMA nodes per socket = NPS1 [ACPI Settings]
- L3 cache as NUMA = disabled [ACPI Settings]

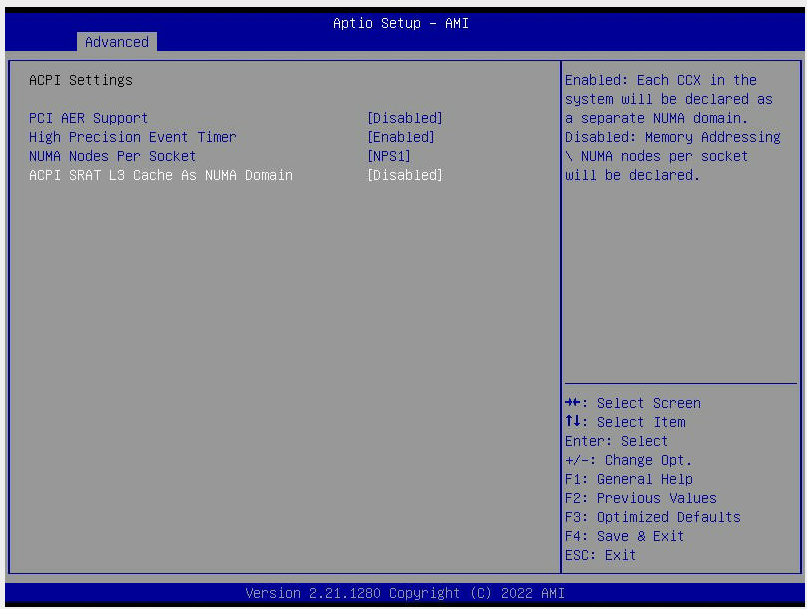
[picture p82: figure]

PCIe Configuration:

- PCIe Relaxed Ordering = enabled [PCIe/PCI/PnP Configuration]


Dr. Alexander Pollak | SETI INSTITUTE | alexander.pollak.87@gmail.com

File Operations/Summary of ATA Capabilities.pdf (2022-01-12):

Sofia Sheikh

# Summary of ATA Capabilities

January 2022 Edition

# Widefield terminology examples

Survey Space; Subarray Positions

ATA Field of
View

Field of View; Subarray Position; Beamformed Beam; Targeted terminology examples

## Organizational Framework for ATA Observing Capabilities

- Two classes of capabilities: Widefield and Targeted
- Each class has multiple modes (e.g., call them W1, W2 and so on for Widefield)
- Each mode is on some current “version”, which tells us how many antennas/ beams/etc. we’re capable of using right now (e.g., W1v1)
- Going from an incoherent sum of 20 antennas to 25 antennas, but otherwise the same mode, would be a version update to that mode
- Adding a new mode is also possible, as time goes on (e.g., a raster scanning survey mode under “Widefield”)

# Summary of Current Capabilities

- Widefield
- W1: Use multiple subarrays, each made of multiple antennas incoherently summed, to tile a survey space within the field of view
- v1: 5 antennas/subarray, 4 subarrays
- Targeted
- T1: Use multiple antennas, incoherently sum all of them into a single subarray centered on a target-of-interest
- v1: 20 antennas
- T2: Use multiple antennas, beamform them at bore-sight onto a target of interest
- v1: 20 antennas

# Short-Term Upcoming Capabilities

- Targeted
- T3: Use multiple antennas, beamform them into a single beam, not at boresight, onto a target-of-interest
- T4: Use multiple antennas, beamform them into a multiple beams across the subarray position, onto multiple targets-of-interest

# Long-Term Upcoming Capabilities

- Widefield
- W2: Use multiple subarrays, each made of multiple antennas incoherently summed, to raster-scan a survey space within the field of view
- Targeted
- T5: Use multiple antennas, beamform them into multiple beams within the subarray position, then change the beam locations mid-observation

## Matching Science Projects to Current Capabilities

- Want to pick projects that are:
A. novel
B. allow us to test the instrument’s current capabilities
C. move us towards developing the instrument’s new capabilities
D. relatively short, for quick “prototyping” cycles

## Matching Science Projects to Current Capabilities

| Novelty | Tests mode to fullest? | Future capability development | Time to complete

W1v1
RFI Survey | HCRO needs a high-frequency resolution RFI survey | Yes | Will inform future observing campaigns | Short
Tile the Galactic Center | Unique at high frequencies? | Yes | ? | Medium

T1v1
Anti-Solar Point Campaign | Untested technique, gives an ETZ survey for free | Yes | ? | Looong, and benefits from more antennas -wait until longer cycles?

T2v1
FRB Repeater Observations | ATA can do unique measurements of repeaters, esp. at high frequencies | Yes | Can be used to test T3 | Short

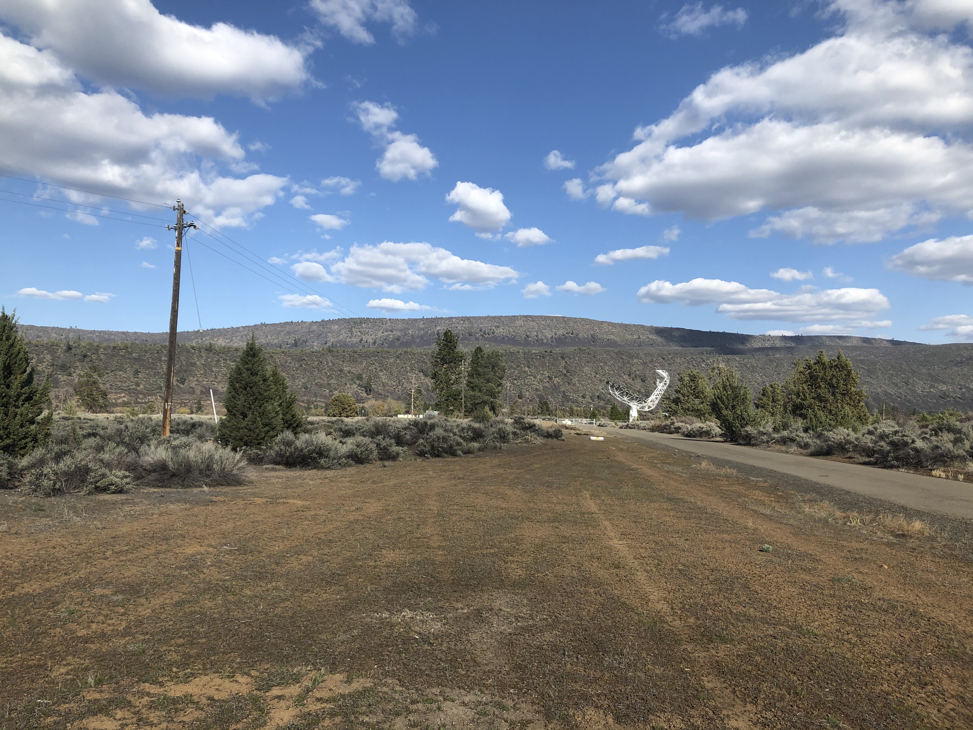
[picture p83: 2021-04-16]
HCRO/HCRO-Building-Summary/Pictures/IMG_0269.jpeg

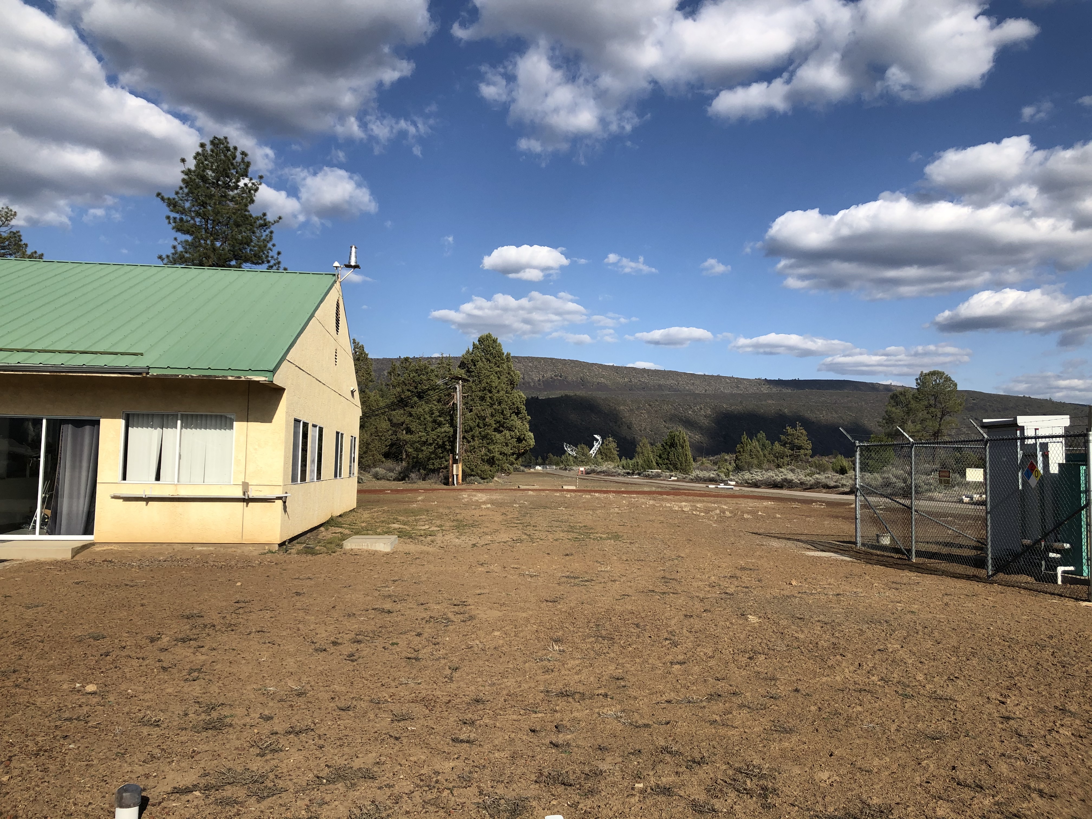
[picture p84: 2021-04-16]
HCRO/HCRO-Building-Summary/Pictures/IMG_0285.jpeg

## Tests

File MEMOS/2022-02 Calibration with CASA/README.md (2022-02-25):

# Calibrating with ATA RFSoC correlator

This document explains how to use CASA to calibrate data using the Realtime correlator with the Allen Telescope Array

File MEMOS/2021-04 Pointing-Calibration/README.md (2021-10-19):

# Pointing calibration with the ATA
This repository would hopefully and ultimately give a clear description of what should be done to perform a pointing calibration for the ATA dishes with the current SNAP/RFSoC digital backend.

## Pointing sheet:
A sheet detailing the pointing calibration done so far:
https://docs.google.com/spreadsheets/d/1RfIvCNcYLlwfeb1UWsOEJo4LyswW3o2lVI1ycjOJ1qk/edit?usp=sharing

Please contact Wael Farah for an "edit" link

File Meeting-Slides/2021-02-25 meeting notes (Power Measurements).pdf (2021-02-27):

# General Update

# - SRI transmits today at 17:00

# - SPR - Ordered cable management for Analog Racks

# - VNA measurement of RFCBs - Investigate IF ripples

# - Power measurement after RF 4-way splitter - Power measurement after RF 4-way splitter using CW

# - H/C measurements with new antennas (repeated) - Test Antenna 3C (020)

Feed List | Feed Revision Overview
Number | Installed Ant. | Tip-Link: R03 | Temp S. Isolation | New Harness | Bellow Removed | Cryo Tuned | Firmware 5.4 | Gold-Plated | Preconditioned Coax
5C4-002 | Feed Lab
5C4-003 | Feed Lab | | x | x | x | x | x
5C4-004 | 2B | x | x | x | x | x | x | x | x
5C4-005 | 2A
5C4-006 | 4J | x | x | x | x | x | x | x | x
5C4-007 | 3L | x | x | x | x | x | x | x | x
5C4-008 | Feed Lab (1G) | | x | x | x | x | x
5C4-009 | Feed Lab | | x | x | x | x | x
5C4-010 | Feed Lab | MINEX | x | x | x | x | x | x | MINEX
5C4-011 | Feed Lab (3L) | MINEX | x | x | x | x | x | x | MINEX
5C4-012 | 1K | x | x | x | x | x | x | x | NA
5C4-013 | 1H | x | x | x | x | x | x | x | x
5C4-014 | Feed Lab (2J) | MINEX | x | x | x | x | x | x | MINEX
5C4-015 | Feed Lab | | x | x | x | x | x
5C4-016 | 2E | x | x | x | x | x | x | x | x
5C4-017 | Feed Lab | | x | x | x | In Progress | x
5C4-018 | 2H | x | x | x | x | x | x | x | NA
5C4-019 | 1C | | x | x | x | x
5C4-020 | 3C | x | x | x | x | x | x | x | x

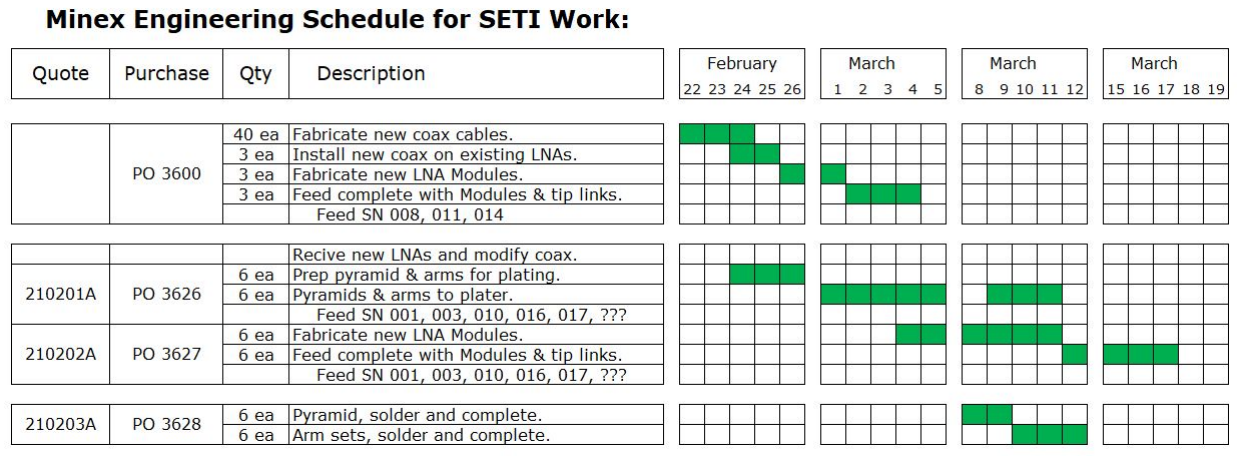
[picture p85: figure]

# RFSoC

# - Found SD card slot

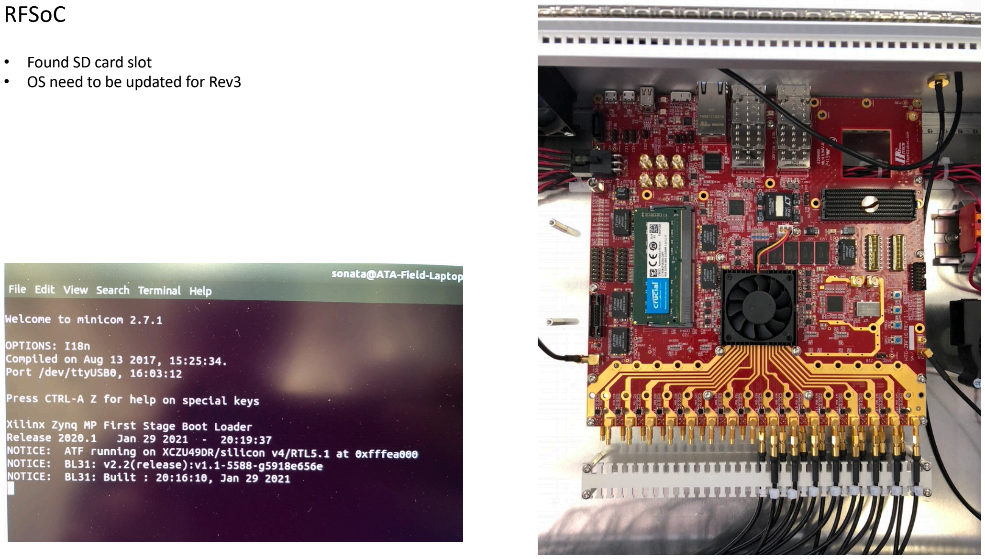
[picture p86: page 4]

# - OS need to be updated for Rev3

# Tsys Measurements with FieldFox

# - 3 measurements per day

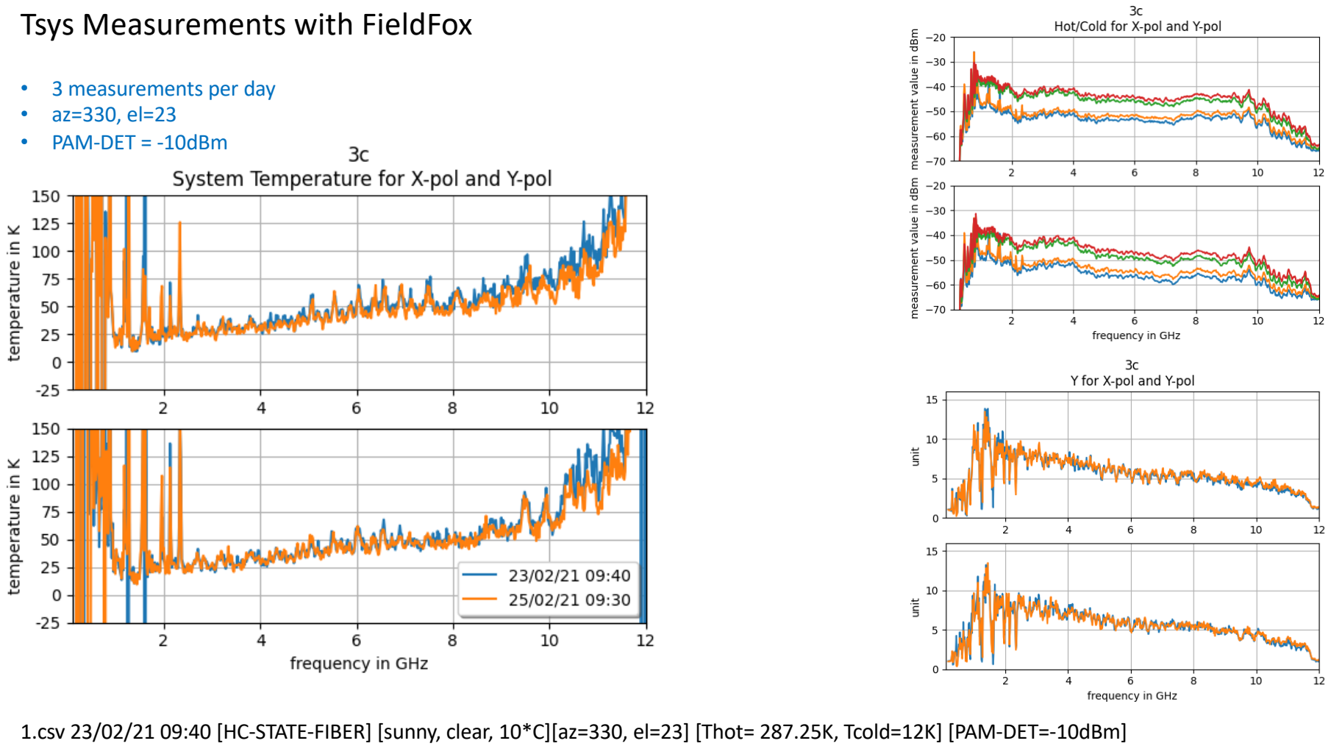
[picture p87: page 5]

# - az=330, el=23 - PAM-DET = -10dBm

1.csv 23/02/21 09:40 [HC-STATE-FIBER] [sunny, clear, 10*C][az=330, el=23] [Thot= 287.25K, Tcold=12K] [PAM-DET=-10dBm]

# Tsys Measurements with FieldFox

# - 3 measurements per day

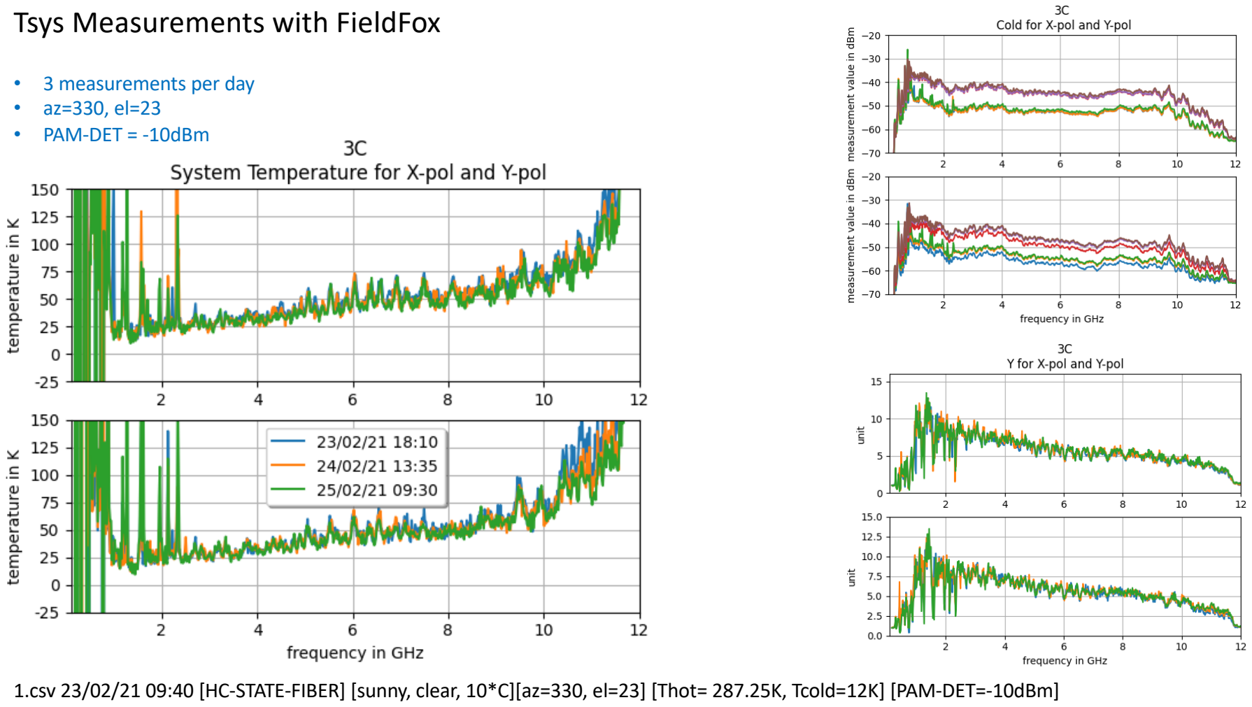
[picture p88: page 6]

# - az=330, el=23 - PAM-DET = -10dBm

1.csv 23/02/21 09:40 [HC-STATE-FIBER] [sunny, clear, 10*C][az=330, el=23] [Thot= 287.25K, Tcold=12K] [PAM-DET=-10dBm]

# Power Measurement

# Verify Cascaded Gain Model!

# Two Measurements:

Sky as input.
CW as input.
Component | Gain dB | Power at this | Dynamic | Y-factor | Tsys | Notes
stage (dBm) | (P1dB) | Range (dB) | (K)
CMB | 0.000 | -92.53 | - | - | 2.70 | 2.700
Atmosphere | -0.060 | -89.30 | - | - | 5.76 | 5.761
Dish | -0.020 | -88.40 | - | - | 7.12 | 7.118
Mirror | -0.020 | -87.66 | - | - | 8.48 | 8.481
Radome | 0.000 | -87.66 | - | - | 8.48 | 8.481
Feed | -0.040 | -87.32 | - | - | 9.24 | 9.239
Link-Capacitor | -0.300 | -85.48 | - | - | 15.15 | 15.148
Cable1 | -0.100 | -85.02 | - | - | 17.21 | 17.210
LNA | 38.000 | -43.38 | -10.00 | 33.38 | 39.86 | 39.858 | LNF Low Noise Amplifier
SS cable | -1.500 | -44.87 | - | - | 39.86 | 39.864
Feedthu SMA | -0.100 | -44.97 | - | - | 39.87 | 39.865 | Output of the cryostat.
SS cable | -2.000 | -46.97 | - | - | 39.91 | 39.909
Bandwith red. 12/15 GHz | -1.000 | -47.97 | - | - | 39.91 | 39.909
NDA-412 | 12.000 | -35.93 | 14.00 | 49.93 | 40.24 | 40.235 | Amplifier
Filter | -3.000 | -38.93 | - | - | 40.24 | 40.235 | High Pass Filter
HMC424 | -4.000 | -42.93 | 22.00 | 64.93 | 40.24 | 40.235 | Variable attenuator 0-31.5dB
NDA-412 | 12.000 | -30.92 | 14.00 | 44.92 | 40.34 | 40.339 | Amplifier
Slope Compensator | -2.000 | -32.92 | - | - | 40.34 | 40.339
NDA-412 | 12.000 | -20.92 | 14.00 | 34.92 | 40.35 | 40.349 | Amplifier
Slope Compensator | -2.000 | -22.92 | - | - | 40.35 | 40.349
NDA-412 | 12.000 | -10.92 | 14.00 | 24.92 | 40.35 | 40.350 | Amplifier
HMC424 | -20.000 | -30.92 | 22.00 | 52.92 | 40.35 | 40.350 | Variable attenuator 0-31.5dB
NDA-412 | 12.000 | -18.92 | 14.00 | 32.92 | 40.36 | 40.356 | Amplifier
Slope Compensator | -2.000 | -20.92 | - | - | 40.36 | 40.356
NDA-412 | 12.000 | -8.92 | 14.00 | 22.92 | 40.36 | 40.357 | Amplifier
PAM output cable to OTX | 0.000 | -8.92 | - | - | 40.36 | 40.357 | Measured by detector diode
NX8560LJ-CC189 | 0.000 | -8.92 | 11.60 | 20.52 | 40.36 | 40.357 | Fiber Transmitter
Fiber cable | -35.000 | -43.86 | - | - | 40.89 | 40.892 | Fiber Link
DSC-40S | 0.000 | -43.86 | - | - | 40.89 | 40.892 | Fiber Detector
NDA-412 | 12.000 | -31.85 | 14.00 | 45.85 | 41.02 | 41.021 | Amplifier
NDA-412 | 12.000 | -19.85 | 14.00 | 33.85 | 41.03 | 41.030 | Amplifier
NDA-412 | 12.000 | -7.85 | 14.00 | 21.85 | 41.03 | 41.030 | Amplifier
4-way Wilkinson Divider | -6.000 | -13.85 | - | - | 41.03 | 41.030 | Power Divider
NDA-412 | 12.000 | -1.85 | 14.00 | 15.85 | 41.03 | 41.030 | Amplifier
Stepped Impedance Filter | -1.000 | -2.85 | - | - | 41.03 | 41.030 | LPF
Fixed Attenuator | -10.000 | -12.85 | - | - | 41.03 | 41.030 | Fixed Attenuator
HMC260 | -7.500 | -20.35 | 12.00 | 32.35 | 41.03 | 41.030 | Mixer UP
BPF 700MHz | -3.500 | -23.85 | - | - | 41.03 | 41.031 | Filter
Bandwith red. 0.7/12 GHz | -12.300 | -36.15 | - | - | 41.03 | 41.031
HMC516 | 20.500 | -15.65 | 14.00 | 29.65 | 41.04 | 41.037 | Amplifier
HMC412 | -8.000 | -23.65 | 11.50 | 35.15 | 41.04 | 41.037 | Mixer DOWN
SGA-2286 | 15.000 | -8.65 | 8.30 | 16.95 | 41.04 | 41.038 | Amplifier
RFCB output cable | -0.100 | -8.75 | - | - | 41.04 | 41.038
LMR-240 25ft | -1.500 | -10.25 | - | - | 41.04 | 41.038
AA06-xxH | -10.000 | -20.25 | - | - | 41.04 | 41.038 | Fixed Attenuator
ZX60-43-S+ | 22.000 | 1.75 | 17.30 | 15.55 | 41.04 | 41.039 | Amplifier
ZX76-31R5A-SPS+ | -19.000 | -17.25 | 22.00 | 39.25 | 41.04 | 41.039 | Variable attenuator 0-31.5dB
AFX-CA-141-xx | -0.100 | -17.35 | - | - | 41.04 | 41.039
EVA8AQ160 ADC | -0.050 | -17.40 | 0.00 | 17.40 | 41.04 | 41.039 | SNAP ADC

# Power Measurement

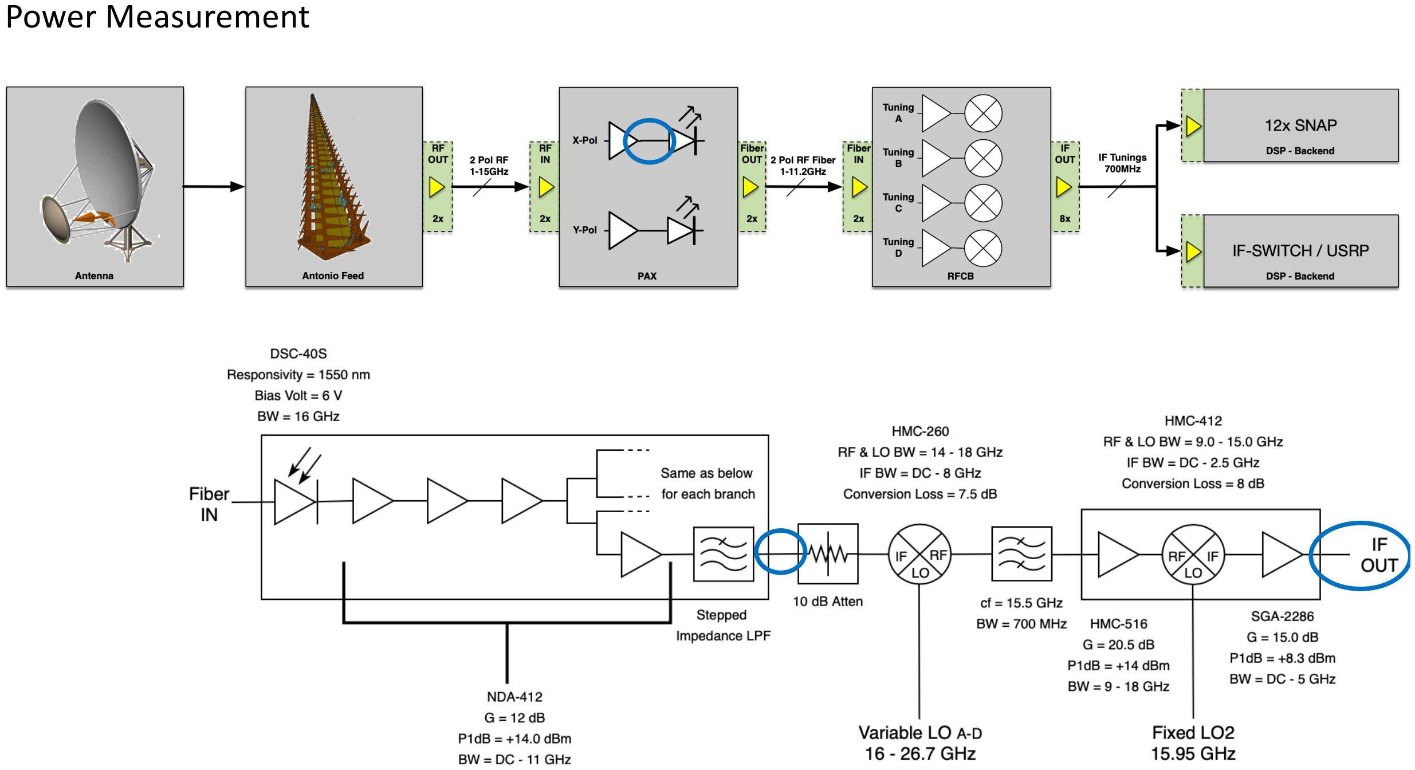
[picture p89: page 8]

# Power Measurement

# - Sky input:

# - Initial measurement

Component | Gain dB | Power at this | Measured | Dynamic
stage (dBm) | Power (dBm) | (P1dB) | Range (dB)
Bandwith red. 12/15 GHz NDA-412 Filter HMC424 NDA-412 Slope Compensator NDA-412 Slope Compensator NDA-412 HMC424 NDA-412 Slope Compensator NDA-412 PAM output cable to OTX NX8560LJ-CC189 | -1.000 12.000 -3.000 -4.000 12.000 -2.000 12.000 -2.000 12.000 -20.000 12.000 -2.000 12.000 0.000 0.000 | -47.97 -35.93 -38.93 -42.93 -30.92 -32.92 -20.92 -22.92 -10.92 -30.92 -18.92 -20.92 -8.92 -8.92 -8.92 | -10.10 | -14.00 -22.00 14.00 -14.00 -14.00 22.00 14.00 -14.00 -11.60 | -49.93 -64.93 44.92 -34.92 -24.92 52.92 32.92 -22.92 -20.52
Fiber cable | -35.000 | -43.86 | | - | -
DSC-40S NDA-412 NDA-412 NDA-412 4-way Wilkinson Divider NDA-412 Stepped Impedance Filter Fixed Attenuator HMC260 BPF 700MHz Bandwith red. 0.7/12 GHz HMC516 HMC412 SGA-2286 RFCB output cable | 0.000 12.000 12.000 12.000 -6.000 12.000 -1.000 -10.000 -7.500 -3.500 -12.300 20.500 -8.000 15.000 -0.100 | -43.86 -31.85 -19.85 -7.85 -13.85 -1.85 -2.85 -12.85 -20.35 -23.85 -36.15 -15.65 -23.65 -8.65 -8.75 | -2.70 0.0|-8.0|-12.2|-8.6 | -14.00 14.00 14.00 -14.00 --12.00 --14.00 11.50 8.30 - | -45.85 33.85 21.85 -15.85 --32.35 --29.65 35.15 16.95 -

# 1GHz | 2GHz | 5GHz | 10GHz

Component | Gain dB | Power at this | Measured | Dynamic
stage (dBm) | Power (dBm) | (P1dB) | Range (dB)
Bandwith red. 12/15 GHz NDA-412 Filter HMC424 NDA-412 Slope Compensator NDA-412 Slope Compensator NDA-412 HMC424 NDA-412 Slope Compensator NDA-412 PAM output cable to OTX NX8560LJ-CC189 | -1.000 12.000 -3.000 -5.000 12.000 -2.000 12.000 -2.000 12.000 -20.000 12.000 -2.000 12.000 0.000 0.000 | -47.97 -35.93 -38.93 -43.93 -31.92 -33.92 -21.92 -23.92 -11.92 -31.92 -19.92 -21.92 -9.92 -9.92 -9.92 | -10.10 | -14.00 -22.00 14.00 -14.00 -14.00 22.00 14.00 -14.00 -11.60 | -49.93 -65.93 45.92 -35.92 -25.92 53.92 33.92 -23.92 -21.52
Fiber cable | -35.000 | -44.85 | | - | -
DSC-40S NDA-412 NDA-412 NDA-412 4-way Wilkinson Divider NDA-412 Stepped Impedance Filter Fixed Attenuator HMC260 BPF 700MHz Bandwith red. 0.7/12 GHz HMC516 HMC412 SGA-2286 RFCB output cable | 0.000 12.000 12.000 12.000 -6.000 12.000 -1.000 -10.000 -7.500 -3.500 -12.300 20.500 -8.000 15.000 -0.100 | -44.85 -32.83 -20.83 -8.83 -14.83 -2.83 -3.83 -13.83 -21.33 -24.83 -37.13 -16.63 -24.63 -9.63 -9.73 | -2.70 0.0|-8.0|-12.2|-8.6 | -14.00 14.00 14.00 -14.00 --12.00 --14.00 11.50 8.30 - | -46.83 34.83 22.83 -16.83 --33.33 --30.63 36.13 17.93 -

# Power Measurement

# - Sky input:

# - Corrected measurement

# 1GHz | 2GHz | 5GHz | 10GHz

# Power Measurement

# - Sky input:

# - Dynamic range based on RF power setting:

Measurement | Component | Measured | Dynamic
Power (dBm) | (P1dB) | Range (dB)

#1

PAM output cable to OTX | -18.4 | 11.60 | 30.00
Output RFCB power splitter | -10.2 | 13 | 23.20
RFCB out @ 1GHz | -8.0 | 8.3 | 16.30
RFCB out @ 2GHz | -15.5 | 8.3 | 23.80
RFCB out @ 5GHz | -20.3 | 8.3 | 28.60
RFCB out @ 10GHz | -16.1 | 8.3 | 24.40

#2

PAM output cable to OTX | -14.8 | 11.60 | 26.40
Output RFCB power splitter | -7.0 | 13 | 20.00
RFCB out @ 1GHz | -5.0 | 8.3 | 13.30
RFCB out @ 2GHz | -12.2 | 8.3 | 20.50
RFCB out @ 5GHz | -16.6 | 8.3 | 24.90
RFCB out @ 10GHz | -12.9 | 8.3 | 21.20

#3

PAM output cable to OTX | -10.1 | 11.60 | 21.70
Output RFCB power splitter | -2.7 | 13 | 15.70
RFCB out @ 1GHz | 0.0 | 8.3 | 8.30
RFCB out @ 2GHz | -8.0 | 8.3 | 16.30
RFCB out @ 5GHz | -12.2 | 8.3 | 20.50
RFCB out @ 10GHz | -8.6 | 8.3 | 16.90

#4

PAM output cable to OTX | -4.8 | 11.60 | 16.40
Output RFCB power splitter | 2.7 | 13 | 10.30
RFCB out @ 1GHz | 4.0 | 8.3 | 4.30
RFCB out @ 2GHz | -2.4 | 8.3 | 10.70
RFCB out @ 5GHz | -6.7 | 8.3 | 15.00
RFCB out @ 10GHz | -3.4 | 8.3 | 11.70

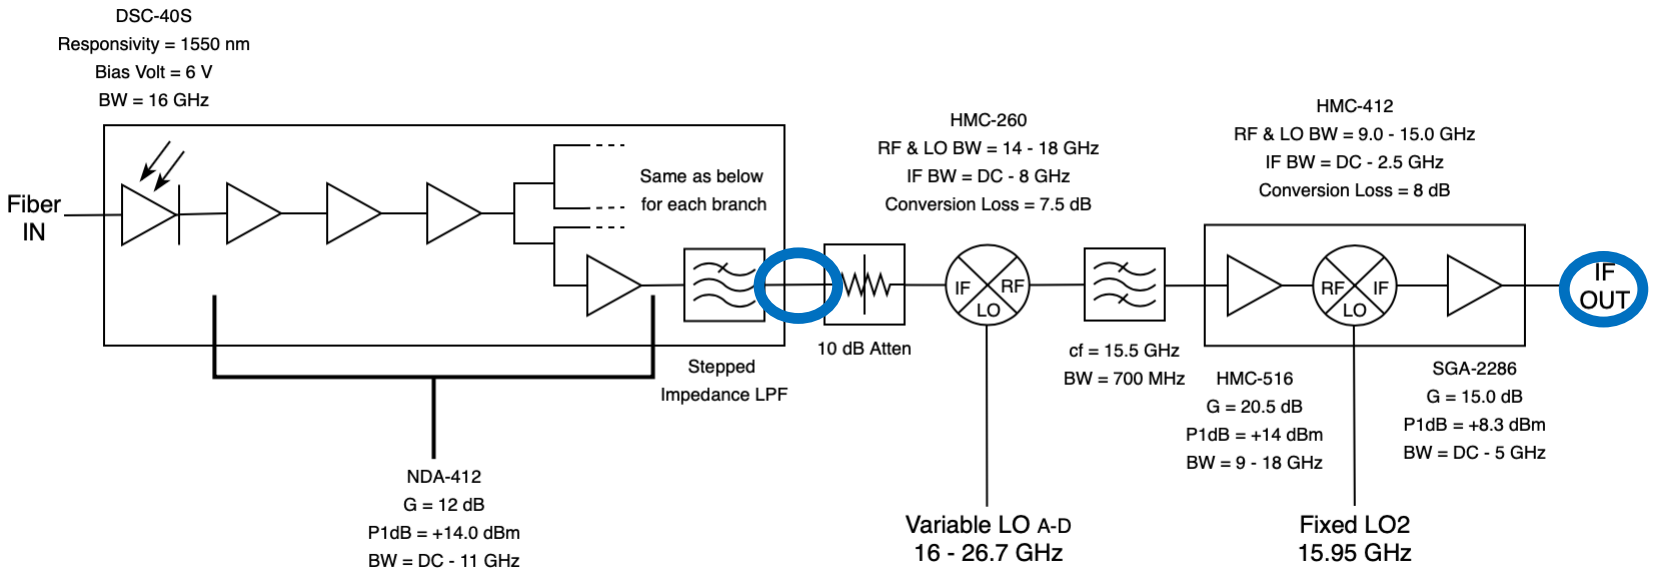
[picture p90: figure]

#5

PAM output cable to OTX | 0.3 | 11.60 | 11.30
Output RFCB power splitter | 7.4 | 13 | 5.60
RFCB out @ 1GHz | 8.5 | 8.3 | -0.20
RFCB out @ 2GHz | 2.2 | 8.3 | 6.10
RFCB out @ 5GHz | -1.9 | 8.3 | 10.20
RFCB out @ 10GHz | 1.6 | 8.3 | 6.70

### Sky input measurement

# Power Measurement

# - CW input:

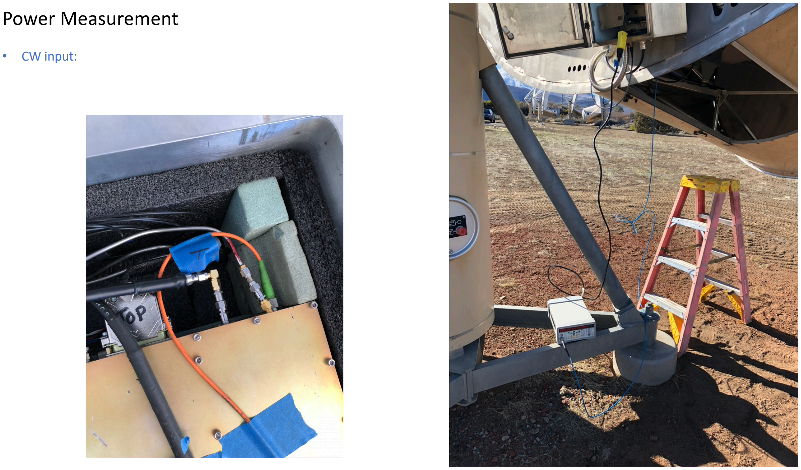
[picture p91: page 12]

# Power Measurement

# - CW input:

# - Dynamic range based on RF power setting:

Measurement | Component | Measured | Dynamic
Power (dBm) | (P1dB) | Range (dB)

#1

PAM output cable to OTX | -18.2 | 11.60 | 29.80
Output RFCB power splitter | -12.5 | 13 | 25.50
RFCB out @ 2GHz | -2.4 | 8.3 | 10.70
RFCB out @ 5GHz | -30.0 | 8.3 | 38.30

#2

PAM output cable to OTX | -15.4 | 11.60 | 27.00
Output RFCB power splitter | -9.7 | 13 | 22.70
RFCB out @ 2GHz | 0.3 | 8.3 | 8.00
RFCB out @ 5GHz | -27.0 | 8.3 | 35.30

#3

PAM output cable to OTX | -9.8 | 11.60 | 21.40
Output RFCB power splitter | -4.3 | 13 | 17.30
RFCB out @ 2GHz | 5.8 | 8.3 | 2.50
RFCB out @ 5GHz | -22.8 | 8.3 | 31.10

#4

PAM output cable to OTX | -4.7 | 11.60 | 16.30
Output RFCB power splitter | 1.0 | 13 | 12.00
RFCB out @ 2GHz | 10.7 | 8.3 | -2.40
RFCB out @ 5GHz | -17.0 | 8.3 | 25.30

#5

PAM output cable to OTX | -0.2 | 11.60 | 11.80
Output RFCB power splitter | 5.9 | 13 | 7.10
RFCB out @ 2GHz | 13.0 | 8.3 | -4.70
RFCB out @ 5GHz | -12.0 | 8.3 | 20.30

### CW input measurement @2.1GHz

# Power Measurement

# - NEXT:

# - Tsys decrease based on RF Power setting for: -10dBm, -15dBm, -20dBm

# - Agree on minimum required dynamic range: e.g.: 10dB?

Component | Power (dBm) Tsys | Tsys Increase
(dBm) | (Kelvin) | (Kelvin)

#1

PAM output cable to OTX | -5.0 | 40.5 | 0.00
PAM output cable to OTX | -10.0 | 41.0 | 0.50
PAM output cable to OTX | -15.0 | 43.0 | 2.50
PAM output cable to OTX | -20.0 | 50.0 | 9.50
PAM output cable to OTX | -25.0 | 72.0 | 31.50

# Tsys based on PAX output power

# Other issues discovered during measurement:

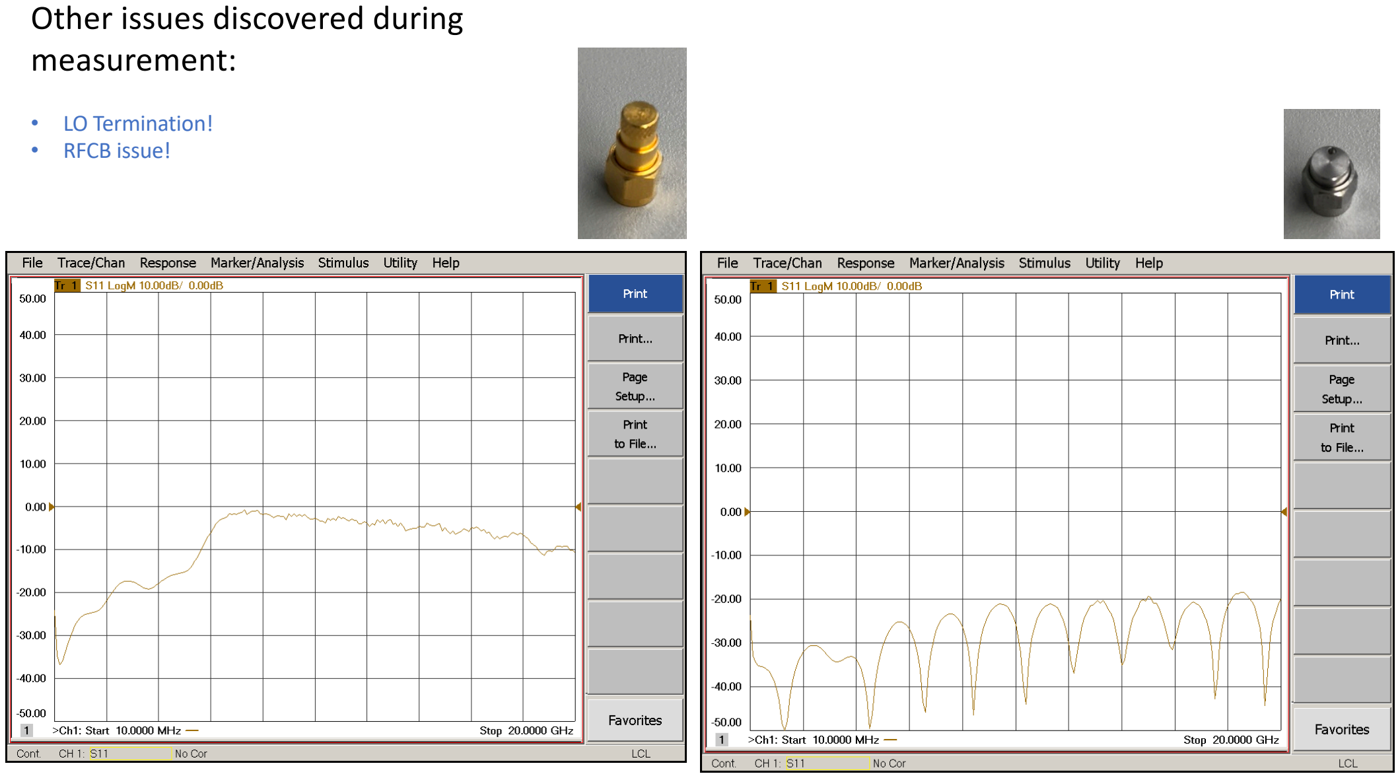
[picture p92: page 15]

# - LO Termination! - RFCB issue!

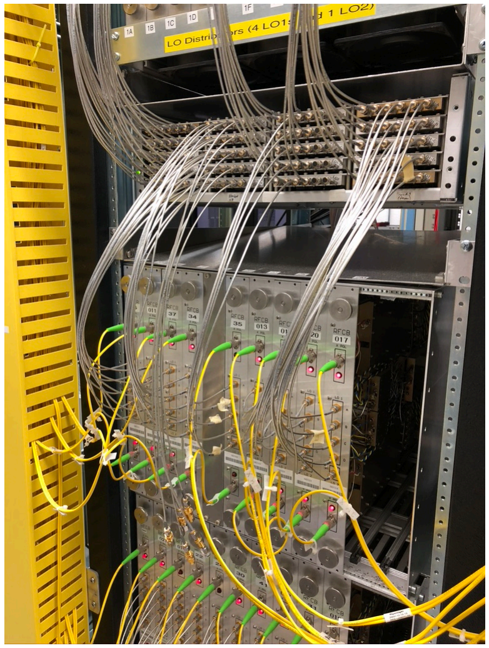
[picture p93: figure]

# Other issues discovered during measurement:

# - LO Termination! - RFCB issue!

# Other issues discovered during

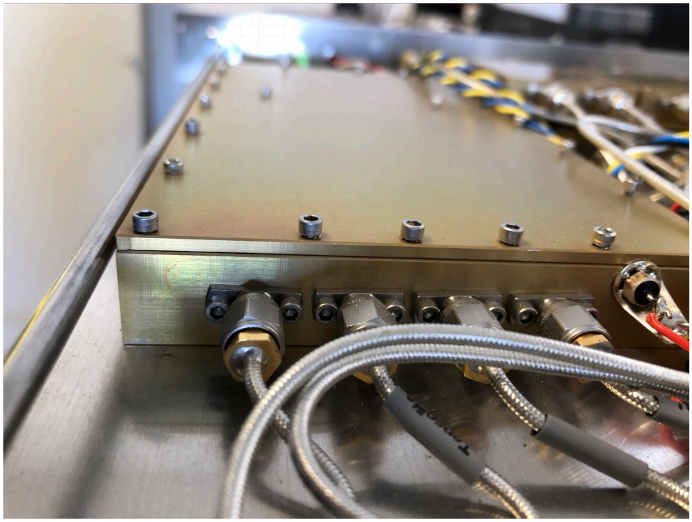
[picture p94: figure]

# measurement:

# - LO Termination! - RFCB issue!

# Attemplifier Board Arrived



# Main Outlets for DSP and Analog Rack Installed

# Parts missing for final build out


# - Feed Base - 4 Glass Domes ORDERED (04/21) - Diaphragm Pumps ARRIVED

# - 2 new build pyramids (20 total) - 6 SS coax cables from LNA to base ORDERED - 3 48V power supplies to be installed at antennas (collected from Minex)

# - 4 LNAs (6 ordered)

# - Feed 002 Base Plate

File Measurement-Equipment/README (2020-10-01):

Datasheets and documents of equipment used for measuring ATA compnenets such as the PAX boxes and the RFCBs.

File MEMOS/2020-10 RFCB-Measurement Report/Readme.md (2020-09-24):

Will be polulated with RFCB Measurement Memo

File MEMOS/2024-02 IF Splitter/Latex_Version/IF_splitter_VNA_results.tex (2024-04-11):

\documentclass[12pt,a4paper,oneside]{article}
\usepackage[margin=1.2in]{geometry}
\usepackage{appendix}
\usepackage[dvips]{graphicx}
\usepackage{epsfig}
\usepackage{amsmath}
\usepackage{amssymb}
\usepackage{psfrag}
\usepackage[square, comma,sort,numbers]{natbib}
\usepackage{fancyhdr}
\usepackage[nottoc]{tocbibind}
\usepackage{color}
\usepackage{fixltx2e}
\usepackage{pdfpages}
\usepackage{pdflscape}
\usepackage{booktabs}
\usepackage{graphicx}
\usepackage{float}
\usepackage{afterpage}
\usepackage{subcaption}
\usepackage{lscape}
\usepackage{rotating}
\usepackage{enumitem}
\usepackage{array,tabularx}
\usepackage{fancyref}
\usepackage[dvipsnames]{xcolor}
\usepackage[colorlinks=true,allcolors=blue]{hyperref}%

\newcommand{\quotes}[1]{``#1''}

\newenvironment{conditions*}
  {\par\vspace{\abovedisplayskip}\noindent
   \tabularx{\columnwidth}{>{$}l<{$} @{\ : } >{\raggedright\arraybackslash}X}}
  {\endtabularx\par\vspace{\belowdisplayskip}}

\pagestyle{fancy}
\title{\Huge The Hat Creek Radio Observatory\\
\vspace{0.5cm}
VNA test results of the IF Splitter\\
\vspace{0.5cm}
\normalsize \emph{}
\vspace{3.5cm}
\begin{center}

\end{center}
}
\author{ 
\vspace{1cm}
\Large
\textbf{ Alexander Pollak \& Marc Jacquart} \\
SETI Institute \\ 
339 Bernardo Ave, Suite 200 \\
Mountain View, CA 94043 \\ 
Alexander.Pollak.87@gmail.com\\
}
\date{\today}

\begin{document}
\clearpage\maketitle
\thispagestyle{empty}
\newpage
\section{General}
This document contains all the scattering matrix measurements done in March-April 2024 during the two IF splitter modules construction to ensure their quality and for further reference. All the measurements were done following the instructions in the ``Testing'' section of ``The IF Splitter'' document.
\vspace{7cm}
\section{Results}

% --- 1Ax_3dB1--- 
\begin{figure}[H]
\centering

\caption{Scattering matrix for channel 1A, polarization x and output 3dB1.}
\label{fig:1Ax_3dB1}
\end{figure}

% --- 1Ax_6dB2--- 
\begin{figure}[H]
\centering

\caption{Scattering matrix for channel 1A, polarization x and output 6dB2.}
\label{fig:1Ax_6dB2}
\end{figure}

% --- 1Ax_6dB3--- 
\begin{figure}[H]
\centering

\caption{Scattering matrix for channel 1A, polarization x and output 6dB3.}
\label{fig:1Ax_6dB3}
\end{figure}

% --- 1Ay_3dB1--- 
\begin{figure}[H]
\centering

\caption{Scattering matrix for channel 1A, polarization y and output 3dB1.}
\label{fig:1Ay_3dB1}
\end{figure}

% --- 1Ay_6dB2--- 
\begin{figure}[H]
\centering

\caption{Scattering matrix for channel 1A, polarization y and output 6dB2.}
\label{fig:1Ay_6dB2}
\end{figure}

% --- 1Ay_6dB3--- 
\begin{figure}[H]
\centering

\caption{Scattering matrix for channel 1A, polarization y and output 6dB3.}
\label{fig:1Ay_6dB3}
\end{figure}

% --- 1Bx_3dB1--- 
\begin{figure}[H]
\centering

\caption{Scattering matrix for channel 1B, polarization x and output 3dB1.}
\label{fig:1Bx_3dB1}
\end{figure}

% --- 1Bx_6dB2--- 
\begin{figure}[H]
\centering

\caption{Scattering matrix for channel 1B, polarization x and output 6dB2.}
\label{fig:1Bx_6dB2}
\end{figure}

% --- 1Bx_6dB3--- 
\begin{figure}[H]
\centering

\caption{Scattering matrix for channel 1B, polarization x and output 6dB3.}
\label{fig:1Bx_6dB3}
\end{figure}

% --- 1By_3dB1--- 
\begin{figure}[H]
\centering

\caption{Scattering matrix for channel 1B, polarization y and output 3dB1.}
\label{fig:1By_3dB1}
\end{figure}

% --- 1By_6dB2--- 
\begin{figure}[H]
\centering

\caption{Scattering matrix for channel 1B, polarization y and output 6dB2.}
\label{fig:1By_6dB2}
\end{figure}

% --- 1By_6dB3--- 
\begin{figure}[H]
\centering

\caption{Scattering matrix for channel 1B, polarization y and output 6dB3.}
\label{fig:1By_6dB3}
\end{figure}

% --- 1Cx_3dB1--- 
\begin{figure}[H]
\centering

\caption{Scattering matrix for channel 1C, polarization x and output 3dB1.}
\label{fig:1Cx_3dB1}
\end{figure}

% --- 1Cx_6dB2--- 
\begin{figure}[H]
\centering

\caption{Scattering matrix for channel 1C, polarization x and output 6dB2.}
\label{fig:1Cx_6dB2}
\end{figure}

% --- 1Cx_6dB3--- 
\begin{figure}[H]
\centering

\caption{Scattering matrix for channel 1C, polarization x and output 6dB3.}
\label{fig:1Cx_6dB3}
\end{figure}

% --- 1Cy_3dB1--- 
\begin{figure}[H]
\centering

\caption{Scattering matrix for channel 1C, polarization y and output 3dB1.}
\label{fig:1Cy_3dB1}
\end{figure}

% --- 1Cy_6dB2--- 
\begin{figure}[H]
\centering

\caption{Scattering matrix for channel 1C, polarization y and output 6dB2.}
\label{fig:1Cy_6dB2}
\end{figure}

% --- 1Cy_6dB3--- 
\begin{figure}[H]
\centering

\caption{Scattering matrix for channel 1C, polarization y and output 6dB3.}
\label{fig:1Cy_6dB3}
\end{figure}

% --- 1Dx_3dB1--- 
\begin{figure}[H]
\centering

\caption{Scattering matrix for channel 1D, polarization x and output 3dB1.}
\label{fig:1Dx_3dB1}
\end{figure}

% --- 1Dx_6dB2--- 
\begin{figure}[H]
\centering

\caption{Scattering matrix for channel 1D, polarization x and output 6dB2.}
\label{fig:1Dx_6dB2}
\end{figure}

% --- 1Dx_6dB3--- 
\begin{figure}[H]
\centering

\caption{Scattering matrix for channel 1D, polarization x and output 6dB3.}
\label{fig:1Dx_6dB3}
\end{figure}

% --- 1Dy_3dB1--- 
\begin{figure}[H]
\centering

\caption{Scattering matrix for channel 1D, polarization y and output 3dB1.}
\label{fig:1Dy_3dB1}
\end{figure}

% --- 1Dy_6dB2--- 
\begin{figure}[H]
\centering

\caption{Scattering matrix for channel 1D, polarization y and output 6dB2.}
\label{fig:1Dy_6dB2}
\end{figure}

% --- 1Dy_6dB3--- 
\begin{figure}[H]
\centering

\caption{Scattering matrix for channel 1D, polarization y and output 6dB3.}
\label{fig:1Dy_6dB3}
\end{figure}

% --- 1Ex_3dB1--- 
\begin{figure}[H]
\centering

\caption{Scattering matrix for channel 1E, polarization x and output 3dB1.}
\label{fig:1Ex_3dB1}
\end{figure}

% --- 1Ex_6dB2--- 
\begin{figure}[H]
\centering

\caption{Scattering matrix for channel 1E, polarization x and output 6dB2.}
\label{fig:1Ex_6dB2}
\end{figure}

% --- 1Ex_6dB3--- 
\begin{figure}[H]
\centering

\caption{Scattering matrix for channel 1E, polarization x and output 6dB3.}
\label{fig:1Ex_6dB3}
\end{figure}

% --- 1Ey_3dB1--- 
\begin{figure}[H]
\centering

\caption{Scattering matrix for channel 1E, polarization y and output 3dB1.}
\label{fig:1Ey_3dB1}
\end{figure}

% --- 1Ey_6dB2--- 
\begin{figure}[H]
\centering

\caption{Scattering matrix for channel 1E, polarization y and output 6dB2.}
\label{fig:1Ey_6dB2}
\end{figure}

% --- 1Ey_6dB3--- 
\begin{figure}[H]
\centering

\caption{Scattering matrix for channel 1E, polarization y and output 6dB3.}
\label{fig:1Ey_6dB3}
\end{figure}

% --- 1Fx_3dB1--- 
\begin{figure}[H]
\centering

\caption{Scattering matrix for channel 1F, polarization x and output 3dB1.}
\label{fig:1Fx_3dB1}
\end{figure}

% --- 1Fx_6dB2--- 
\begin{figure}[H]
\centering

\caption{Scattering matrix for channel 1F, polarization x and output 6dB2.}
\label{fig:1Fx_6dB2}
\end{figure}

% --- 1Fx_6dB3--- 
\begin{figure}[H]
\centering

\caption{Scattering matrix for channel 1F, polarization x and output 6dB3.}
\label{fig:1Fx_6dB3}
\end{figure}

% --- 1Fy_3dB1--- 
\begin{figure}[H]
\centering

\caption{Scattering matrix for channel 1F, polarization y and output 3dB1.}
\label{fig:1Fy_3dB1}
\end{figure}

% --- 1Fy_6dB2--- 
\begin{figure}[H]
\centering

\caption{Scattering matrix for channel 1F, polarization y and output 6dB2.}
\label{fig:1Fy_6dB2}
\end{figure}

% --- 1Fy_6dB3--- 
\begin{figure}[H]
\centering

\caption{Scattering matrix for channel 1F, polarization y and output 6dB3.}
\label{fig:1Fy_6dB3}
\end{figure}

% --- 1Gx_3dB1--- 
\begin{figure}[H]
\centering

\caption{Scattering matrix for channel 1G, polarization x and output 3dB1.}
\label{fig:1Gx_3dB1}
\end{figure}

% --- 1Gx_6dB2--- 
\begin{figure}[H]
\centering

\caption{Scattering matrix for channel 1G, polarization x and output 6dB2.}
\label{fig:1Gx_6dB2}
\end{figure}

% --- 1Gx_6dB3--- 
\begin{figure}[H]
\centering

\caption{Scattering matrix for channel 1G, polarization x and output 6dB3.}
\label{fig:1Gx_6dB3}
\end{figure}

% --- 1Gy_3dB1--- 
\begin{figure}[H]
\centering

\caption{Scattering matrix for channel 1G, polarization y and output 3dB1.}
\label{fig:1Gy_3dB1}
\end{figure}

% --- 1Gy_6dB2--- 
\begin{figure}[H]
\centering

\caption{Scattering matrix for channel 1G, polarization y and output 6dB2.}
\label{fig:1Gy_6dB2}
\end{figure}

% --- 1Gy_6dB3--- 
\begin{figure}[H]
\centering

\caption{Scattering matrix for channel 1G, polarization y and output 6dB3.}
\label{fig:1Gy_6dB3}
\end{figure}

% --- 1Hx_3dB1--- 
\begin{figure}[H]
\centering

\caption{Scattering matrix for channel 1H, polarization x and output 3dB1.}
\label{fig:1Hx_3dB1}
\end{figure}

% --- 1Hx_6dB2--- 
\begin{figure}[H]
\centering

\caption{Scattering matrix for channel 1H, polarization x and output 6dB2.}
\label{fig:1Hx_6dB2}
\end{figure}

% --- 1Hx_6dB3--- 
\begin{figure}[H]
\centering

\caption{Scattering matrix for channel 1H, polarization x and output 6dB3.}
\label{fig:1Hx_6dB3}
\end{figure}

% --- 1Hy_3dB1--- 
\begin{figure}[H]
\centering

\caption{Scattering matrix for channel 1H, polarization y and output 3dB1.}
\label{fig:1Hy_3dB1}
\end{figure}

% --- 1Hy_6dB2--- 
\begin{figure}[H]
\centering

\caption{Scattering matrix for channel 1H, polarization y and output 6dB2.}
\label{fig:1Hy_6dB2}
\end{figure}

% --- 1Hy_6dB3--- 
\begin{figure}[H]
\centering

\caption{Scattering matrix for channel 1H, polarization y and output 6dB3.}
\label{fig:1Hy_6dB3}
\end{figure}

% --- 1Jx_3dB1--- 
\begin{figure}[H]
\centering

\caption{Scattering matrix for channel 1J, polarization x and output 3dB1.}
\label{fig:1Jx_3dB1}
\end{figure}

% --- 1Jx_6dB2--- 
\begin{figure}[H]
\centering

\caption{Scattering matrix for channel 1J, polarization x and output 6dB2.}
\label{fig:1Jx_6dB2}
\end{figure}

% --- 1Jx_6dB3--- 
\begin{figure}[H]
\centering

\caption{Scattering matrix for channel 1J, polarization x and output 6dB3.}
\label{fig:1Jx_6dB3}
\end{figure}

% --- 1Jy_3dB1--- 
\begin{figure}[H]
\centering

\caption{Scattering matrix for channel 1J, polarization y and output 3dB1.}
\label{fig:1Jy_3dB1}
\end{figure}

% --- 1Jy_6dB2--- 
\begin{figure}[H]
\centering

\caption{Scattering matrix for channel 1J, polarization y and output 6dB2.}
\label{fig:1Jy_6dB2}
\end{figure}

% --- 1Jy_6dB3--- 
\begin{figure}[H]
\centering

\caption{Scattering matrix for channel 1J, polarization y and output 6dB3.}
\label{fig:1Jy_6dB3}
\end{figure}

% --- 1Kx_3dB1--- 
\begin{figure}[H]
\centering

\caption{Scattering matrix for channel 1K, polarization x and output 3dB1.}
\label{fig:1Kx_3dB1}
\end{figure}

% --- 1Kx_6dB2--- 
\begin{figure}[H]
\centering

\caption{Scattering matrix for channel 1K, polarization x and output 6dB2.}
\label{fig:1Kx_6dB2}
\end{figure}

% --- 1Kx_6dB3--- 
\begin{figure}[H]
\centering

\caption{Scattering matrix for channel 1K, polarization x and output 6dB3.}
\label{fig:1Kx_6dB3}
\end{figure}

% --- 1Ky_3dB1--- 
\begin{figure}[H]
\centering

\caption{Scattering matrix for channel 1K, polarization y and output 3dB1.}
\label{fig:1Ky_3dB1}
\end{figure}

% --- 1Ky_6dB2--- 
\begin{figure}[H]
\centering

\caption{Scattering matrix for channel 1K, polarization y and output 6dB2.}
\label{fig:1Ky_6dB2}
\end{figure}

% --- 1Ky_6dB3--- 
\begin{figure}[H]
\centering

\caption{Scattering matrix for channel 1K, polarization y and output 6dB3.}
\label{fig:1Ky_6dB3}
\end{figure}

% --- 2Ax_3dB1--- 
\begin{figure}[H]
\centering

\caption{Scattering matrix for channel 2A, polarization x and output 3dB1.}
\label{fig:2Ax_3dB1}
\end{figure}

% --- 2Ax_6dB2--- 
\begin{figure}[H]
\centering

\caption{Scattering matrix for channel 2A, polarization x and output 6dB2.}
\label{fig:2Ax_6dB2}
\end{figure}

% --- 2Ax_6dB3--- 
\begin{figure}[H]
\centering

\caption{Scattering matrix for channel 2A, polarization x and output 6dB3.}
\label{fig:2Ax_6dB3}
\end{figure}

% --- 2Ay_3dB1--- 
\begin{figure}[H]
\centering

\caption{Scattering matrix for channel 2A, polarization y and output 3dB1.}
\label{fig:2Ay_3dB1}
\end{figure}

% --- 2Ay_6dB2--- 
\begin{figure}[H]
\centering

\caption{Scattering matrix for channel 2A, polarization y and output 6dB2.}
\label{fig:2Ay_6dB2}
\end{figure}

% --- 2Ay_6dB3--- 
\begin{figure}[H]
\centering

\caption{Scattering matrix for channel 2A, polarization y and output 6dB3.}
\label{fig:2Ay_6dB3}
\end{figure}

% --- 2Bx_3dB1--- 
\begin{figure}[H]
\centering

\caption{Scattering matrix for channel 2B, polarization x and output 3dB1.}
\label{fig:2Bx_3dB1}
\end{figure}

% --- 2Bx_6dB2--- 
\begin{figure}[H]
\centering

\caption{Scattering matrix for channel 2B, polarization x and output 6dB2.}
\label{fig:2Bx_6dB2}
\end{figure}

% --- 2Bx_6dB3--- 
\begin{figure}[H]
\centering

\caption{Scattering matrix for channel 2B, polarization x and output 6dB3.}
\label{fig:2Bx_6dB3}
\end{figure}

% --- 2By_3dB1--- 
\begin{figure}[H]
\centering

\caption{Scattering matrix for channel 2B, polarization y and output 3dB1.}
\label{fig:2By_3dB1}
\end{figure}

% --- 2By_6dB2--- 
\begin{figure}[H]
\centering

\caption{Scattering matrix for channel 2B, polarization y and output 6dB2.}
\label{fig:2By_6dB2}
\end{figure}

% --- 2By_6dB3--- 
\begin{figure}[H]
\centering

\caption{Scattering matrix for channel 2B, polarization y and output 6dB3.}
\label{fig:2By_6dB3}
\end{figure}

% --- 2Cx_3dB1--- 
\begin{figure}[H]
\centering

\caption{Scattering matrix for channel 2C, polarization x and output 3dB1.}
\label{fig:2Cx_3dB1}
\end{figure}

% --- 2Cx_6dB2--- 
\begin{figure}[H]
\centering

\caption{Scattering matrix for channel 2C, polarization x and output 6dB2.}
\label{fig:2Cx_6dB2}
\end{figure}

% --- 2Cx_6dB3--- 
\begin{figure}[H]
\centering

\caption{Scattering matrix for channel 2C, polarization x and output 6dB3.}
\label{fig:2Cx_6dB3}
\end{figure}

% --- 2Cy_3dB1--- 
\begin{figure}[H]
\centering

\caption{Scattering matrix for channel 2C, polarization y and output 3dB1.}
\label{fig:2Cy_3dB1}
\end{figure}

% --- 2Cy_6dB2--- 
\begin{figure}[H]
\centering

\caption{Scattering matrix for channel 2C, polarization y and output 6dB2.}
\label{fig:2Cy_6dB2}
\end{figure}

% --- 2Cy_6dB3--- 
\begin{figure}[H]
\centering

\caption{Scattering matrix for channel 2C, polarization y and output 6dB3.}
\label{fig:2Cy_6dB3}
\end{figure}

% --- 2Dx_3dB1--- 
\begin{figure}[H]
\centering

\caption{Scattering matrix for channel 2D, polarization x and output 3dB1.}
\label{fig:2Dx_3dB1}
\end{figure}

% --- 2Dx_6dB2--- 
\begin{figure}[H]
\centering

\caption{Scattering matrix for channel 2D, polarization x and output 6dB2.}
\label{fig:2Dx_6dB2}
\end{figure}

% --- 2Dx_6dB3--- 
\begin{figure}[H]
\centering

\caption{Scattering matrix for channel 2D, polarization x and output 6dB3.}
\label{fig:2Dx_6dB3}
\end{figure}

% --- 2Dy_3dB1--- 
\begin{figure}[H]
\centering

\caption{Scattering matrix for channel 2D, polarization y and output 3dB1.}
\label{fig:2Dy_3dB1}
\end{figure}

% --- 2Dy_6dB2--- 
\begin{figure}[H]
\centering

\caption{Scattering matrix for channel 2D, polarization y and output 6dB2.}
\label{fig:2Dy_6dB2}
\end{figure}

% --- 2Dy_6dB3--- 
\begin{figure}[H]
\centering

\caption{Scattering matrix for channel 2D, polarization y and output 6dB3.}
\label{fig:2Dy_6dB3}
\end{figure}

% --- 2Ex_3dB1--- 
\begin{figure}[H]
\centering

\caption{Scattering matrix for channel 2E, polarization x and output 3dB1.}
\label{fig:2Ex_3dB1}
\end{figure}

% --- 2Ex_6dB2--- 
\begin{figure}[H]
\centering

\caption{Scattering matrix for channel 2E, polarization x and output 6dB2.}
\label{fig:2Ex_6dB2}
\end{figure}

% --- 2Ex_6dB3--- 
\begin{figure}[H]
\centering

\caption{Scattering matrix for channel 2E, polarization x and output 6dB3.}
\label{fig:2Ex_6dB3}
\end{figure}

% --- 2Ey_3dB1--- 
\begin{figure}[H]
\centering

\caption{Scattering matrix for channel 2E, polarization y and output 3dB1.}
\label{fig:2Ey_3dB1}
\end{figure}

% --- 2Ey_6dB2--- 
\begin{figure}[H]
\centering

\caption{Scattering matrix for channel 2E, polarization y and output 6dB2.}
\label{fig:2Ey_6dB2}
\end{figure}

% --- 2Ey_6dB3--- 
\begin{figure}[H]
\centering

\caption{Scattering matrix for channel 2E, polarization y and output 6dB3.}
\label{fig:2Ey_6dB3}
\end{figure}

% --- 2Fx_3dB1--- 
\begin{figure}[H]
\centering

\caption{Scattering matrix for channel 2F, polarization x and output 3dB1.}
\label{fig:2Fx_3dB1}
\end{figure}

% --- 2Fx_6dB2--- 
\begin{figure}[H]
\centering

\caption{Scattering matrix for channel 2F, polarization x and output 6dB2.}
\label{fig:2Fx_6dB2}
\end{figure}

% --- 2Fx_6dB3--- 
\begin{figure}[H]
\centering

\caption{Scattering matrix for channel 2F, polarization x and output 6dB3.}
\label{fig:2Fx_6dB3}
\end{figure}

% --- 2Fy_3dB1--- 
\begin{figure}[H]
\centering

\caption{Scattering matrix for channel 2F, polarization y and output 3dB1.}
\label{fig:2Fy_3dB1}
\end{figure}

% --- 2Fy_6dB2--- 
\begin{figure}[H]
\centering

\caption{Scattering matrix for channel 2F, polarization y and output 6dB2.}
\label{fig:2Fy_6dB2}
\end{figure}

% --- 2Fy_6dB3--- 
\begin{figure}[H]
\centering

\caption{Scattering matrix for channel 2F, polarization y and output 6dB3.}
\label{fig:2Fy_6dB3}
\end{figure}

% --- 2Gx_3dB1--- 
\begin{figure}[H]
\centering

\caption{Scattering matrix for channel 2G, polarization x and output 3dB1.}
\label{fig:2Gx_3dB1}
\end{figure}

% --- 2Gx_6dB2--- 
\begin{figure}[H]
\centering

\caption{Scattering matrix for channel 2G, polarization x and output 6dB2.}
\label{fig:2Gx_6dB2}
\end{figure}
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

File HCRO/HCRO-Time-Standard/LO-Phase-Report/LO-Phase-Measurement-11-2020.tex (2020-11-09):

\documentclass[12pt]{article}
\usepackage[letterpaper, portrait, margin=1in]{geometry}
\usepackage{appendix}
\usepackage[dvips]{graphicx}
\usepackage{epsfig}
\usepackage{amsmath}
\usepackage{amssymb}
\usepackage{psfrag}
\usepackage[square, comma,sort,numbers]{natbib}
\usepackage{fancyhdr}
\usepackage[nottoc]{tocbibind}
\usepackage{color}
\usepackage{fixltx2e}
\usepackage{pdfpages}
\usepackage{pdflscape}
\usepackage{booktabs}
\usepackage{graphicx}
\usepackage{float}
\usepackage{afterpage}
\usepackage{subcaption}
\usepackage{lscape}
\usepackage{rotating}
\usepackage{enumitem}
\usepackage{array,tabularx}
\usepackage{fancyref}
\usepackage[dvipsnames]{xcolor}
\usepackage[colorlinks=true,allcolors=blue]{hyperref}%
\newcommand{\changefont}{%
    \fontsize{9}{11}\selectfont
}
\fancyhf{}
\fancyhead[LE,RO]{\changefont \slshape \rightmark} %section
\fancyhead[RE,LO]{\changefont \slshape \leftmark} %chapter
\fancyfoot[C]{\changefont \thepage} %footer

\newcommand{\quotes}[1]{``#1''}

\newenvironment{conditions*}
  {\par\vspace{\abovedisplayskip}\noindent
   \tabularx{\columnwidth}{>{$}l<{$} @{\ : } >{\raggedright\arraybackslash}X}}
  {\endtabularx\par\vspace{\belowdisplayskip}}

\pagestyle{fancy}
\title{\Huge Allen Telescope Array\\
\vspace{0.5cm}
Local Oscillator\\Phase Modulation Investigation\\
\vspace{1.5cm} %0.5
%\textcolor{red}{“Draft November 05, 2020” }
\normalsize \emph{}
\vspace{1cm} %3
\begin{center}

\end{center}
}
\author{ 

\textbf{ Alexander Pollak} \\
\vspace{1cm}

SETI Institute \\ 
189 Bernardo Ave, Suite 200 \\
Mountain View, CA 94043 \\ 
apollak@seti.org\\
}
\date{\today}

\begin{document}
\clearpage\maketitle
\thispagestyle{empty}

\newpage
\thispagestyle{empty}
\section*{Abstract}

This document provides a description of the measurements and work which has been done to investigate the phase instability of the ATA. The GNU-Radio team who uses the ATA during weekends reported back in October problems with the phase stability of the instrument. 
During their observations of spacecrafts, they noticed a 60\,Hz and 120\,Hz modulation of the carrier signal that made it impossible for them to demodulate any information from said spacecraft. Throughout the investigation we could locate several problems with the time standard generation, distribution, and wiring, which we partly resolved during this process. The modification we implemented as part of this investigation were sufficient to remove the previously observed 60\,Hz and 120\,Hz modulation and the GNU-Radio observers could successfully demodulate information from a spacecraft carrier signal. However, there are still other issues that require further investigations, such as the 1PPS generation and 10MHz distribution to the DSP hardware that are not in the scope of this document.

\noindent 
%

%
%\vspace{3cm}
%\begin{flushright}
%Alexander Pollak \\ \emph{September, 2015}
%\end{flushright}

\newpage
\thispagestyle{empty}
\tableofcontents
\newpage

%----------------------------------------------------------------------------------------
%	SECTION 1
%----------------------------------------------------------------------------------------
%\pagestyle{plain}
\section{GNU-Radio Observed Phase Modulation}
\label{sec:1}
% ----------------------------------------------------------------

The GNU-Radio team was observing some strange phase-modulation problems somewhere in the receiver chain when pointing at a CW carrier from \textit{Tianwen-1} that should be clean. It was determined that the phase modulation was not a series of phase reversals, so it didn't seem to be caused by the Walsh modulation unit. (turned off)
Figure \ref{fig:Tianwen-1}, shows the observed carrier signal of \textit{Tianwen-1} in frequency space, the carrier is located at 0\,Hz in this plot. One can see that there are lots of spectral lines separated by exactly 60\,Hz and every other spectral line is stronger.

%
\begin{figure}[h]
\centering{}
\caption{Tianwen-1 carrier spectra. The CW carrier frequency is set to be at 0\,Hz in this plot.}
\label{fig:Tianwen-1}
\end{figure}
%

The first step in the investigation of this problem done by the GNU-Radio team was to point the ATA at different space crafts to verify that this problem is within the ATA signal path. Targets that were tested were Tianwen-1 (check NASA horizon for RA and DEC) at 8425 MHz, Mars at 8425 MHz (sometimes but not always orbiters can be seen). Also around 2250 MHz pointed almost anywhere (for example, the Moon); Earth orbiting satellites will be seen on the dish sidelobes. The modulation was also visible regardless of whether the USRP was set to internal or external clock. All signals coming from the telescope IF showed this problem. The phase modulation effect was common to both USRPs (in which we typically receive 1hx, 1hy, 4gx, 4gy), and since we were able to correlate signals between different antennas and USRPs without problems, this indicated that the phase modulation must be correlated between antennas and polarizations.

The leading hypothesis to explain this problem at this point was that the modulation must happen in the frequency conversion stages of the ATA. To narrow down if the modulation was confined within one antenna tuning (eg. LOA-D) or common to all tunings we performed a test observation of \ref{fig:Tianwen-1} with following modification. We used antenna 1C and changed the default IF tuning output from tuning D to tuning C and we used antenna 4G with the default IF tuning D. This allowed us to test if the modulation is caused by any one of the two LOs C or D, or if it is common on both tunings, which would indicate that the modulation might be caused by the down-converting LO2.
The result of this measurement showed that the modulation was present in both tunings, hence we investigated LO2. The modification of this test observation was reverted and all antenna IF signals for the GNU-Radio USRPs were provided from tuning D again.

To investigate if LO2 is the cause of the modulation we then replaced the signal generator providing the LO2 local oscillator signal for the ATA frequency conversion stage with the, at that time, unused LOC and observed another spacecraft carrier signal. \textit{Tianwen-1} could not be used, as it was not visible at this time. Figure \ref{fig:GNU-Obs2}, shows the acquired spectrum of the carrier CW signal. One can see two CW carriers at around 2.25 GHz and no 60\,Hz modulation was present.

%
\begin{figure}[h]
\centering{}
\caption{Spectra of an observed spacecraft carrier. The bottom plot shows the spectra with a frequency span of approximately 40\,MHz and the top plot shows the spectra with a frequency span approximately 8\,KHz. Note that the spacecraft carrier signal in the tip plot is not set exactly to be in the center.  }
\label{fig:GNU-Obs2}
\end{figure}
%

After confirming that the cause of the observed modulation was LO2, we started investigating the LO signal generation, phase stability, time reference and wiring. In the next chapters we describe this investigation in more detail, starting with a description of the test equipment and measurement setup.

%----------------------------------------------------------------------------------------
\section{Measurement Setup}
\label{sec:2}
% ----------------------------------------------------------------

This section describes the setup and hardware used to measure the phase noise and FM modulation of the signal generators which are used to provide the local oscillator signal to the ATA frequency conversions stages.
All measurements have been performed with the Field Fox \href{https://www.keysight.com/en/pdx-x201933-pn-N9938A/fieldfox-handheld-microwave-spectrum-analyzer-265-ghz?pm=spc&nid=-32495.1150527&cc=US&lc=eng}{N9938A} spectrum analyzer and the \href{https://www.rohde-schwarz.com/us/product/nrp_s_sn-productstartpage_63493-99587.html}{NRP-18S} power meter. 

We used to two configuration for the spectrum analyzer, a narrow band (10\,Hz frequency span) and a wide band (500\,Hz frequency span) configuration. The exact settings fo the spectrum analyzer for both configurations are shown in Table \ref{tab:spectrumanalyzer}.

\begin{table}[H]
\caption{Spectrum analyzer settings.} % title name of the table
\centering
\begin{tabular}{l | l|l} \hline\hline
Description & Settings Wide Band & Settings Narrow Band 
\\ [0.5ex]
\hline % inserts single-line
Resolution			& 1001 points 	& 1001 points\\
$center{\rm{freq}}$		& 16.012\,GHz 	& 16.012\,GHz\\
$span$				& 500\,Hz 		& 10\,Hz\\
RBW					& 1\,Hz 		& 1\,Hz\\
VBW		 			& 1\,Hz 		& 1\,Hz\\
Attenuator				& Auto 		& Auto\\
File Format			& .csv 		& .csv\\
Average             		& 10 			& 10\\
\hline 
\end{tabular}
\label{tab:spectrumanalyzer}
\end{table}

The various test setups used to measure the phase noise and 60\,Hz modulation are shown in Figure \ref{fig:measurement_setup_overview}. Note that in oder to pin point the problem of the phase noise and 60\,Hz modulation, we also used different combinations of these test setups. All of these measurements however have in common that the spectrum analyzer was always locked to the same 10\,MHz reference as the to be tested signal generator. The drift between the internal oscillator of spectrum analyzer and the oscillator of the to be tested signal generator was so significant that no meaningful measurement was possible without locking them together. In test setups where no external 10\,MHz was present, the spectrum analyzer was connected to the 10\,MHz ref output of the to be testes signal generator directly.
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

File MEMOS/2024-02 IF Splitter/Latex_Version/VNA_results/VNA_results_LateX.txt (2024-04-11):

% --- 1Ax_3dB1--- 
\begin{figure}[H]
\centering
\includegraphics[width=0.9\linewidth]{VNA_results/1Ax_3dB1.png}
\caption{Scattering matrix for channel 1A, polarization x and output 3dB1.}
\label{fig:1Ax_3dB1}
\end{figure}

% --- 1Ax_6dB2--- 
\begin{figure}[H]
\centering
\includegraphics[width=0.9\linewidth]{VNA_results/1Ax_6dB2.png}
\caption{Scattering matrix for channel 1A, polarization x and output 6dB2.}
\label{fig:1Ax_6dB2}
\end{figure}
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

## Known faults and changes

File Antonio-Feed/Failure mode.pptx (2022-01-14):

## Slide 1

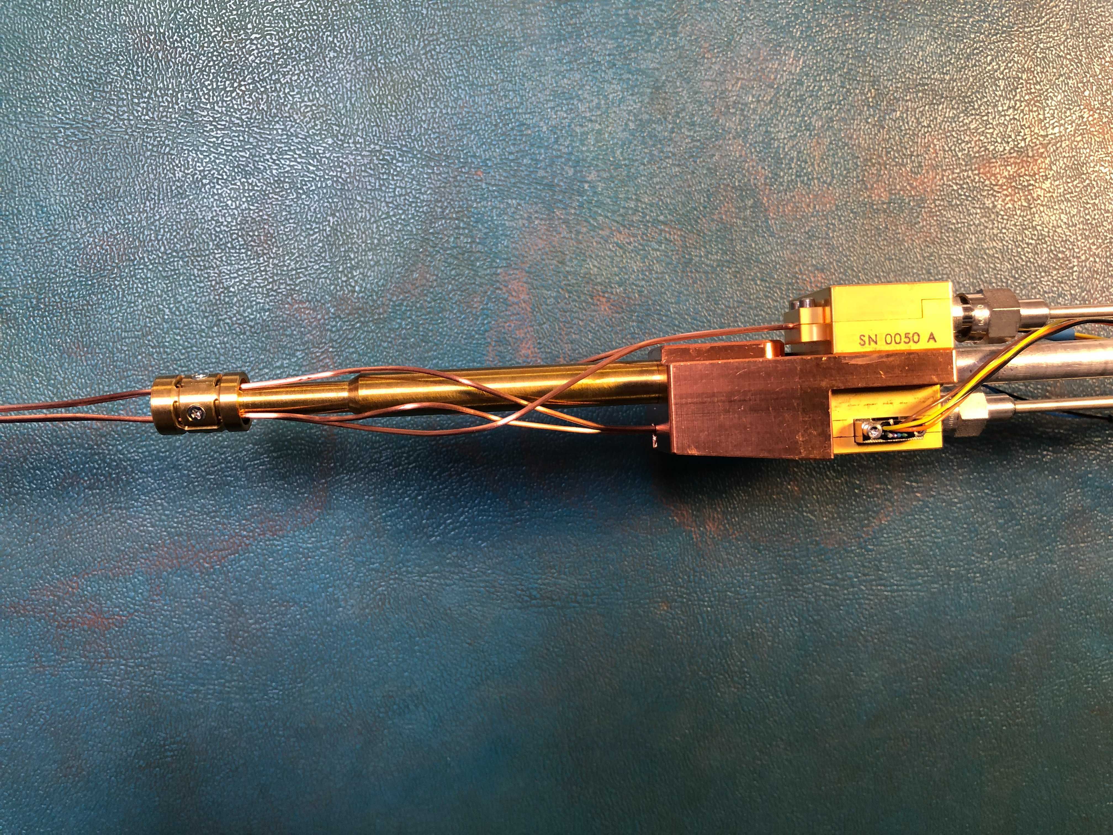
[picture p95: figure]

Those two coaxial cables are 90 deg apart and should go to different LNAs

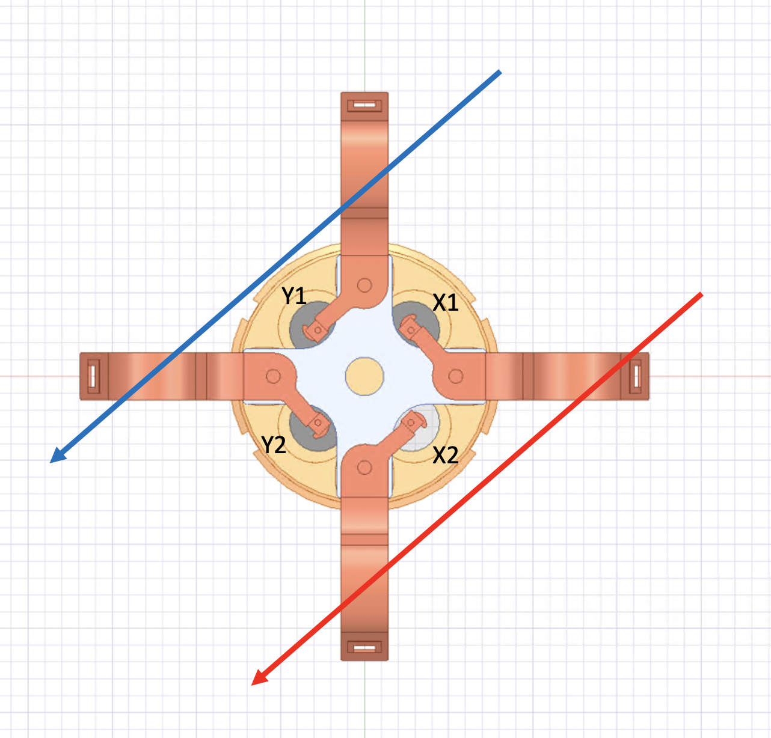
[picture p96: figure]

However they are connected to the same LNA, therefore the differential inputs are wrong.

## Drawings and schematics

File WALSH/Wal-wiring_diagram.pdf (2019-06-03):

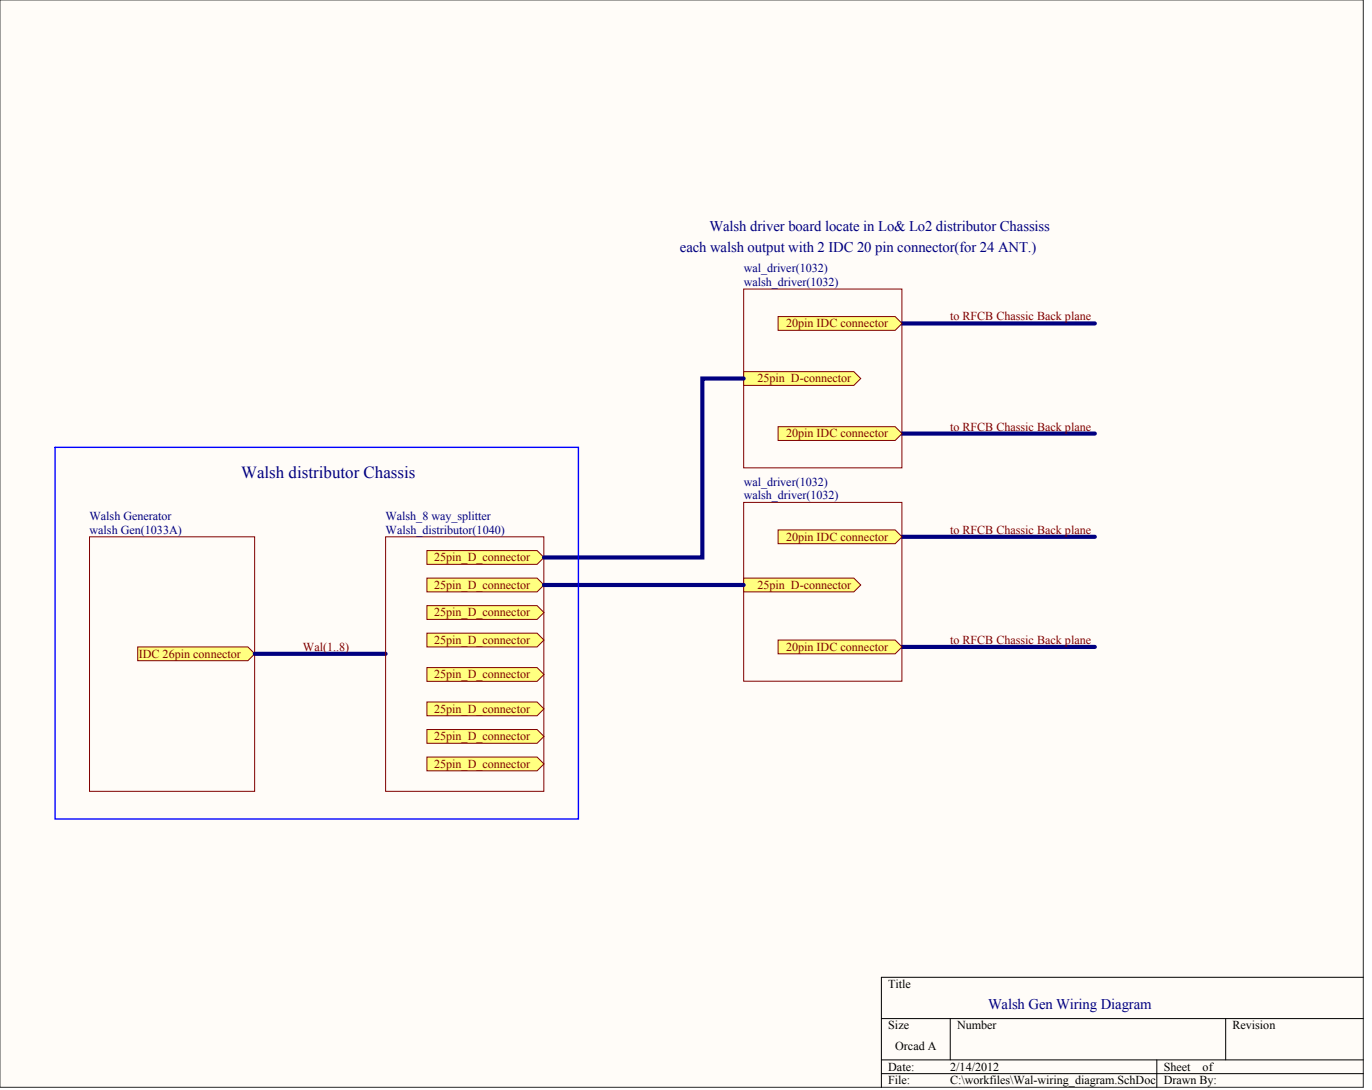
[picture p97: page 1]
Orcad A; Date:; Sheet of; File:; C:\workfiles\Wal-wiring_diagram.SchDoc; Drawn By:; Walsh Generator walsh Gen(1033A); IDC 26pin connector; Wal(1..8); Walsh_8 way_splitter; 20pin IDC connector; 25pin D-connector; P020PIN IDC CONNECTOR

Walsh driver board locate in Lo& Lo2 distributor Chassiss
each walsh output with 2 IDC 20 pin connector(for 24 ANT.)

to RFCB Chassic Back plane

N0TO RFCB CHASSIC BACK PLANE

Walsh distributor Chassis

Walsh Gen Wiring Diagram

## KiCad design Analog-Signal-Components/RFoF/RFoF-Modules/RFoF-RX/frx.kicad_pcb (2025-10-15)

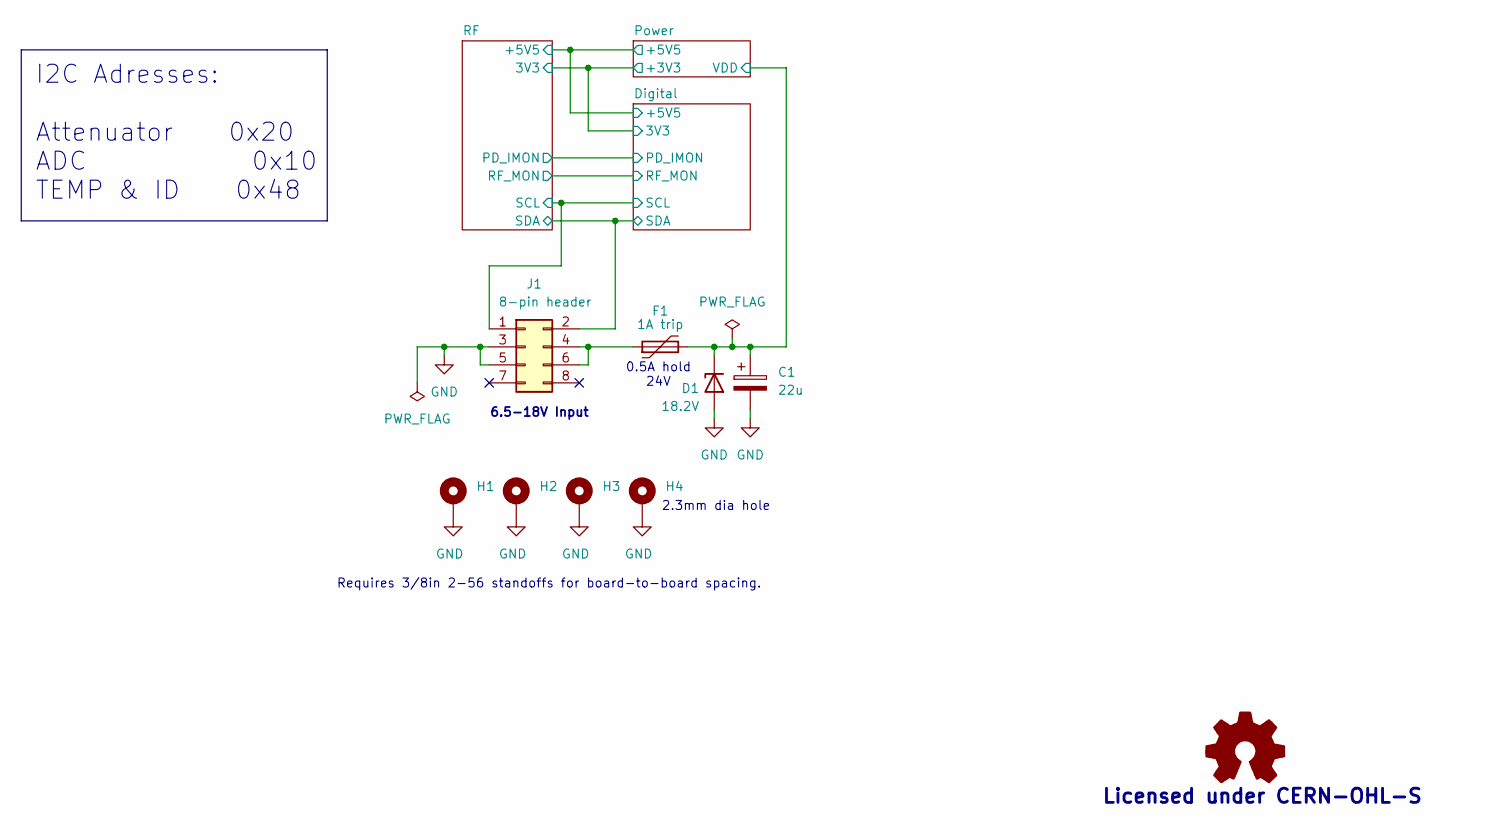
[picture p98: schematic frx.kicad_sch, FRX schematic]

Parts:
C1: 22u; CP_EIA-6032-28_Kemet-C; MPN 293D226X9025C2TE3
D1: 18.2V; D_SMA; MPN SMAJ11A
F1: 1A trip; Fuse_1206_3216Metric; MPN 1206L050/24WR
H1, H2, H3, H4: MountingHole_Pad; MountingHole_2_Pad_Via
J1: 8-pin header; HeaderThru8p; MPN 9-146261-0-04

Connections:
/Digital/SCL: J1.1; also elsewhere on the board
/Digital/SDA: J1.2; also elsewhere on the board
/Power/VDD: C1.1, D1.1 (K), F1.2; also elsewhere on the board
GND: C1.2, D1.2 (A), H1.1, H2.1, H3.1, H4.1, J1.3, J1.5; also elsewhere on the board
unnamed: F1.1, J1.4, J1.6

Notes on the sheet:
Requires 3/8in 2-56 standoffs for board-to-board spacing.
6.5-18V Input
Licensed under CERN-OHL-S
2.3mm dia hole
0.5A hold 24V
I2C Adresses: Attenuator 0x20 ADC 0x10 TEMP & ID 0x48

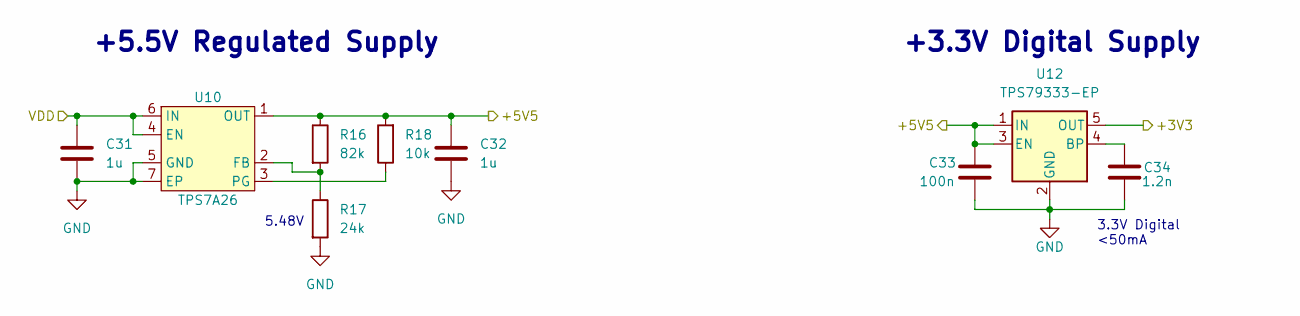
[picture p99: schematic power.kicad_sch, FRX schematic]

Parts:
C31, C32: 1u; C_0603_1608Metric; MPN CL10A105KA8NNNC
C33: 100n; C_0402_1005Metric; MPN CL05B104KP5NNNC
C34: 1.2n; C_0603_1608Metric; MPN GCM1885C1H122JA16D
R16: 82k; R_0402_1005Metric; MPN RC0402FR-0782KL
R17: 24k; R_0402_1005Metric; MPN RC0402FR-0724KL
R18: 10k; R_0402_1005Metric; MPN RC0402FR-0710KL
U10: TPS7A26; WSON-6-1EP_2x2mm_P0.65mm_EP1x1.6mm; MPN TPS7A2601DRVR
U12: TPS79333-EP; SOT-23-5; MPN TPS79333DBVR

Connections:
/Digital/3V3: U12.5 (OUT); also elsewhere on the board
/Digital/+5V5: C32.1, C33.1, R16.1, R18.2, U10.1 (OUT), U12.1 (IN), U12.3 (EN); also elsewhere on the board
/Power/VDD: C31.1, U10.4 (EN), U10.6 (IN); also elsewhere on the board
GND: C31.2, C32.2, C33.2, C34.1, R17.2, U10.5 (GND), U10.7 (EP), U12.2 (GND); also elsewhere on the board
unnamed: R16.2, R17.1, U10.2 (FB)
unnamed: R18.1, U10.3 (PG)
unnamed: C34.2, U12.4 (BP)

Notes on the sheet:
+3.3V Digital Supply
3.3V Digital <50mA
5.48V
+5.5V Regulated Supply

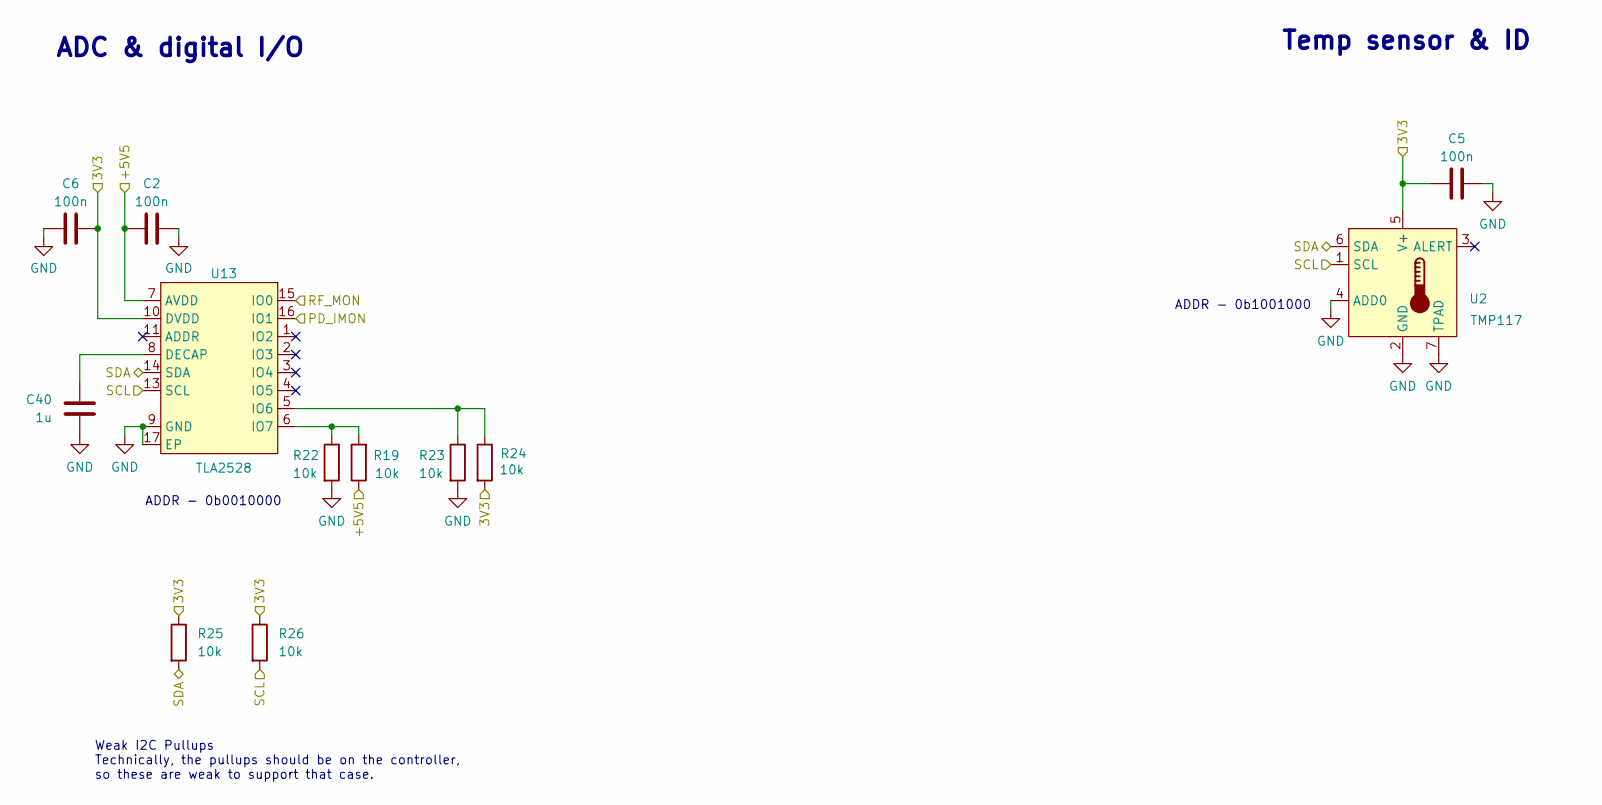
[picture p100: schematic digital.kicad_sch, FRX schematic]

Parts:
C2, C5, C6: 100n; C_0402_1005Metric; MPN CL05B104KP5NNNC
C40: 1u; C_0603_1608Metric; MPN CL10A105KA8NNNC
R19, R22, R23, R24, R25, R26: 10k; R_0402_1005Metric; MPN RC0402FR-0710KL
U2: TMP117; WSON-6-1EP_2x2mm_P0.65mm_EP1x1.6mm; MPN TMP117AIDRVR
U13: TLA2528; WQFN-16-1EP_3x3mm_P0.5mm_EP1.68x1.68mm_LargeThermalVias; MPN TLA2528IRTER

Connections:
/Digital/3V3: C5.2, C6.1, R24.2, R25.1, R26.1, U2.5 (V+), U13.10 (DVDD); also elsewhere on the board
/Digital/+5V5: C2.2, R19.1, U13.7 (AVDD); also elsewhere on the board
/Digital/PD_IMON: U13.16 (IO1); also elsewhere on the board
/Digital/RF_MON: U13.15 (IO0); also elsewhere on the board
/Digital/SCL: R26.2, U2.1 (SCL), U13.13 (SCL); also elsewhere on the board
/Digital/SDA: R25.2, U2.6 (SDA), U13.14 (SDA); also elsewhere on the board
GND: C2.1, C5.1, C6.2, C40.1, R22.2, R23.2, U2.2 (GND), U2.4 (ADD0), U2.7 (TPAD), U13.9 (GND), U13.17 (EP); also elsewhere on the board
unnamed: C40.2, U13.8 (DECAP)
unnamed: R23.1, R24.1, U13.5 (IO6)
unnamed: R19.2, R22.1, U13.6 (IO7)

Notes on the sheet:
Temp sensor & ID
ADDR - 0b1001000
ADC & digital I/O
ADDR - 0b0010000
Weak I2C Pullups Technically, the pullups should be on the controller, so these are weak to support that case.

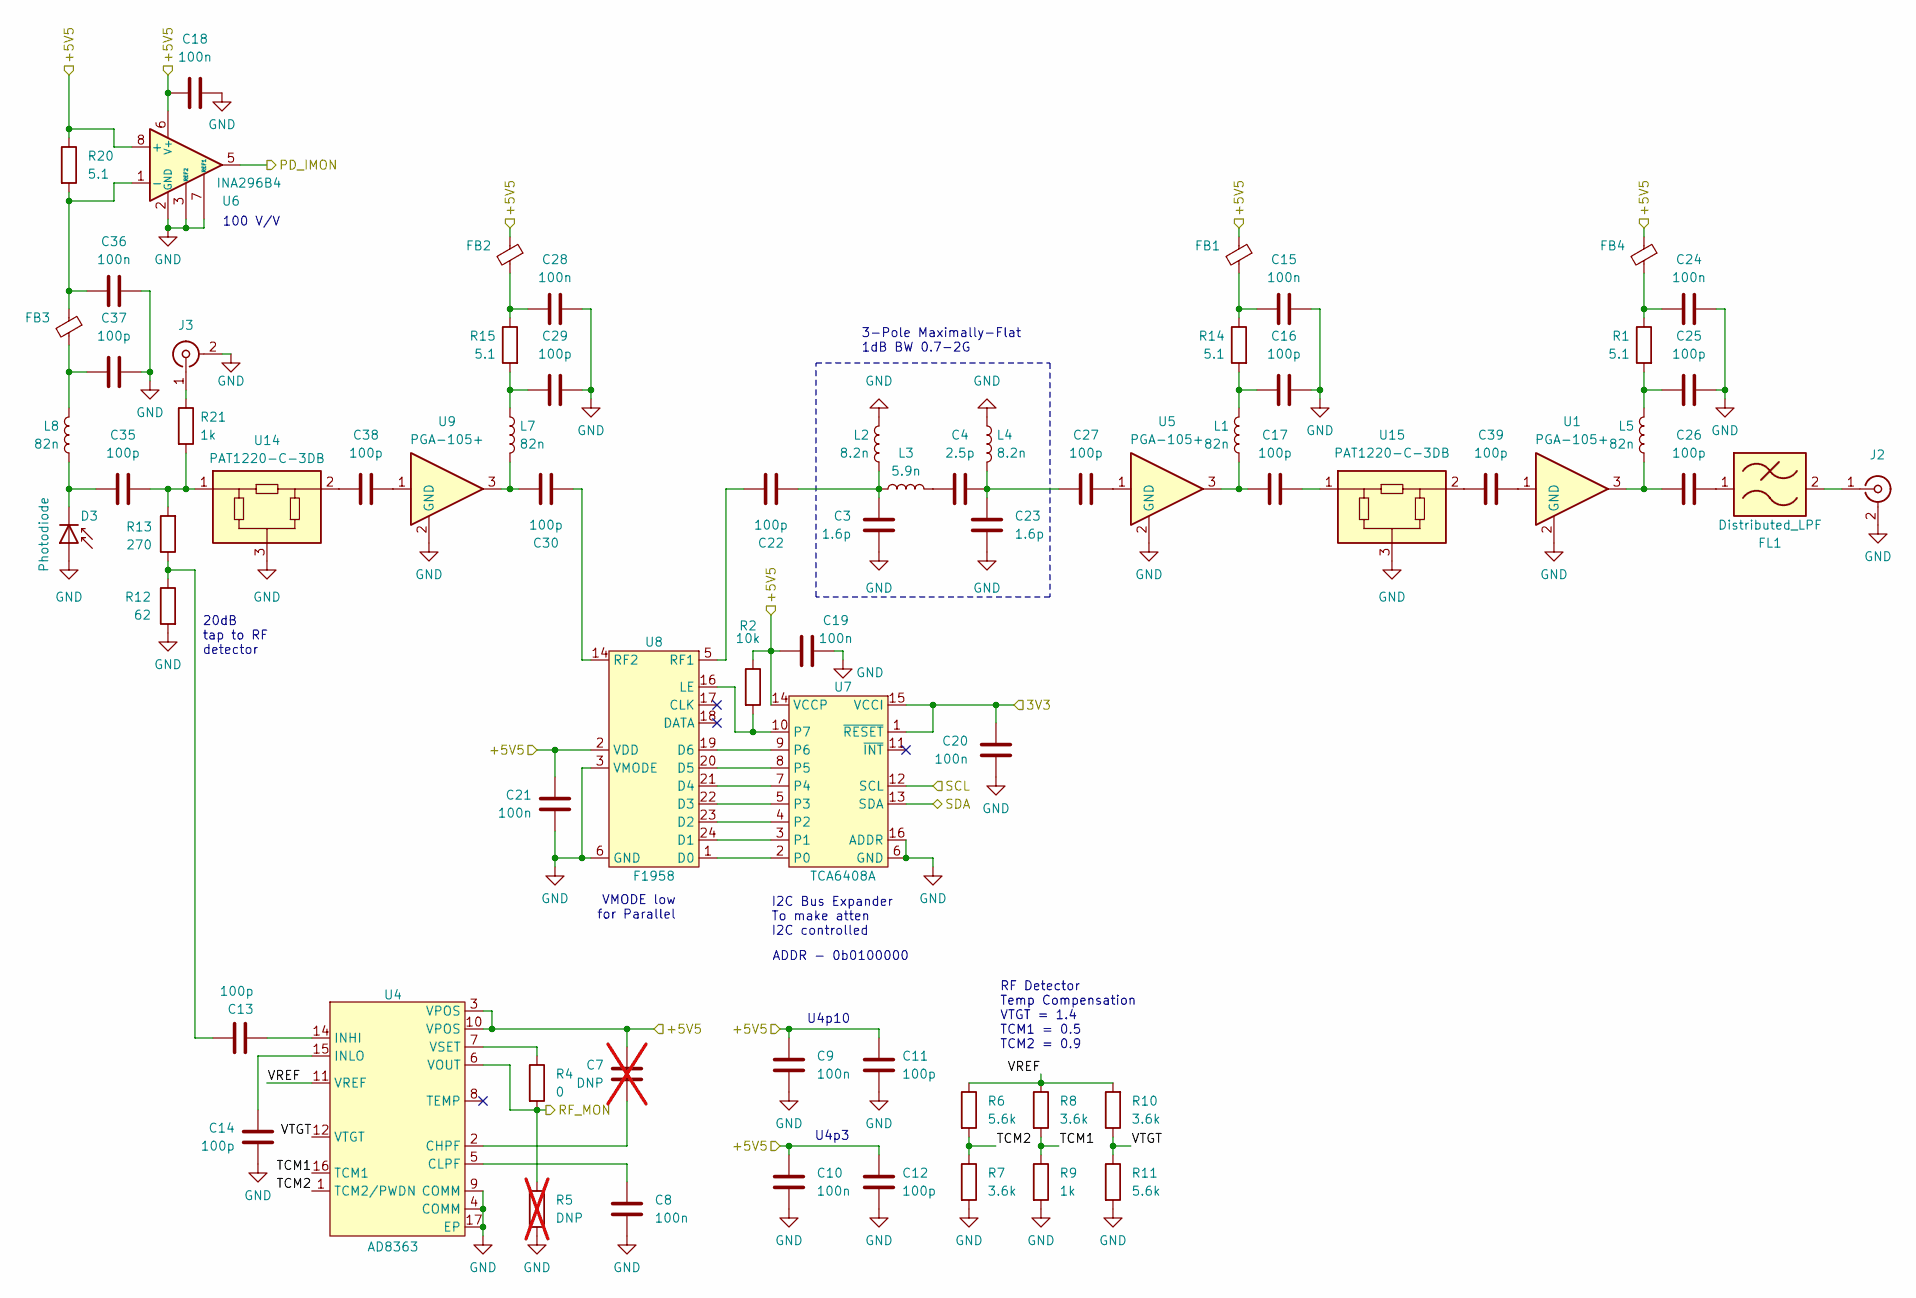
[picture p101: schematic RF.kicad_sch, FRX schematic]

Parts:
C3, C23: 1.6p; C_0402_1005Metric; MPN GJM1555C1H1R6WB01D
C4: 2.5p; C_0402_1005Metric; MPN GJM1555C1H2R5WB01D
C7: DNP; C_0402_1005Metric; not fitted
C8, C9, C10, C15, C18, C19, C20, C21, C24, C28, C36: 100n; C_0402_1005Metric; MPN CL05B104KP5NNNC
C11, C12, C13, C14, C16, C17, C22, C25, C26, C27, C29, C30, C35, C37, C38, C39: 100p; C_0402_1005Metric; MPN CBR04C101J3GAC
D3: Photodiode; MountedPD; MPN PPDA-S
FB1, FB2, FB3, FB4: BLM15PG100SN1D; L_0402_1005Metric; MPN BLM15PG100SN1D
FL1: Distributed_LPF; AA_Filter
J2: Conn_Coaxial; SMP_MSLD_PCT_19; MPN SMP_MSLD_PCT_19
J3: Conn_Coaxial; SMP_EdgeMount_PE44482; MPN PE44482
L1, L5, L7, L8: 82n; L_0402_1005Metric; MPN LQW15AN82NG00D
L2, L4: 8.2n; L_0402_1005Metric; MPN LQW15AN8N2G00D
L3: 5.9n; L_0402_1005Metric; MPN LQW15AN5N9B80D
R1, R20: 5.1; R_0402_1005Metric; MPN RC0402FR-075R1L
R2: 10k; R_0402_1005Metric; MPN RC0402FR-0710KL
R4: 0; R_0402_1005Metric; MPN RC0402FR-070RL
R5: DNP; R_0402_1005Metric; not fitted
R6, R11: 5.6k; R_0402_1005Metric; MPN RC0402FR-075K6L
R7, R8, R10: 3.6k; R_0402_1005Metric; MPN RC0402FR-073K6L
R9, R21: 1k; R_0402_1005Metric; MPN RC0402FR-071KL
R12: 62; R_0402_1005Metric; MPN RC0402FR-0762RL
R13: 270; R_0402_1005Metric; MPN RC0402FR-07270RL
R14, R15: 5.1; R_0402_1005Metric; MPN ERJ-2GEJ5R1X
U1, U5, U9: PGA-105+; SOT89-HighTemp; MPN PGA-105+
U4: AD8363; Analog_LFCSP-16-1EP_4x4mm_P0.65mm_EP2.35x2.35mm_ThermalVias; MPN AD8363ACPZ-R7
U6: INA296B4; SOT-23-8; MPN INA296B4IDDFR
U7: TCA6408A; QFN-16-1EP_3x3mm_P0.5mm_EP1.45x1.45mm; MPN TCA6408ARGTR
U8: F1958; TQFN-24-1EP_4x4mm_P0.5mm_EP2.6x2.6mm_ThermalVias; MPN F1958NBGK
U14, U15: PAT1220-C-3DB; RF_Attenuator_Susumu_PAT1220; MPN PAT1220-C-3DB-T5

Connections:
/Digital/3V3: C20.1, U7.1 (~RESET), U7.15 (VCCI); also elsewhere on the board
/Digital/+5V5: C7.1, C9.1, C10.1, C11.2, C12.2, C18.2, C19.1, C21.1, FB1.1, FB2.1, FB4.1, R2.1, R20.1, U4.3 (VPOS), U4.10 (VPOS), U6.6 (V+), U6.8 (+), U7.14 (VCCP), U8.2 (VDD); also elsewhere on the board
/Digital/PD_IMON: U6.5; also elsewhere on the board
/Digital/RF_MON: R4.2, R5.1, U4.6 (VOUT); also elsewhere on the board
/Digital/SCL: U7.12 (SCL); also elsewhere on the board
/Digital/SDA: U7.13 (SDA); also elsewhere on the board
/RF/TCM1: R8.2, R9.1, U4.16 (TCM1)
/RF/TCM2: R6.2, R7.1, U4.1 (TCM2/PWDN)
/RF/VREF: R6.1, R8.1, R10.2, U4.11 (VREF)
/RF/VTGT: R10.1, R11.1, U4.12 (VTGT)
GND: C3.2, C8.2, C9.2, C10.2, C11.1, C12.1, C14.1, C15.2, C16.2, C18.1, C19.2, C20.2, C21.2, C23.2, C24.2, C25.2, C28.2, C29.2, C36.2, C37.2, D3.2 (A), J2.2 (Ext), J3.2 (Ext), L2.1, L4.1, R5.2, R7.2, R9.2, R11.2, R12.2, U1.2 (GND), U4.4 (COMM), U4.9 (COMM), U4.17 (EP), U5.2 (GND), U6.2 (GND), U6.3 (REF2), U6.4 (GND), U6.7 (REF1), U7.6 (GND), U7.16 (ADDR), U7.17 (GND), U8.3 (VMODE), U8.4 (GND), U8.6 (GND), U8.7 (GND), U8.8 (GND), U8.9 (GND), U8.10 (GND), U8.11 (GND), U8.12 (GND), U8.13 (GND), U8.15 (GND), U8.25 (GND), U9.2 (GND), U14.3, U15.3; also elsewhere on the board
unnamed: C4.1, L3.2
unnamed: C13.2, R12.1, R13.1
unnamed: C15.1, FB1.2, R14.1
unnamed: C16.1, L1.1, R14.2
unnamed: C17.1, L1.2, U5.3
unnamed: C17.2, U15.1
unnamed: C3.1, C22.2, L2.2, L3.1
unnamed: C4.2, C23.1, C27.1, L4.2
unnamed: C24.1, FB4.2, R1.1
unnamed: C25.1, L5.1, R1.2
unnamed: C26.1, L5.2, U1.3
unnamed: C26.2, FL1.1
unnamed: C27.2, U5.1
unnamed: C28.1, FB2.2, R15.1
unnamed: C29.1, L7.1, R15.2
unnamed: C30.1, L7.2, U9.3
unnamed: C35.2, R13.2, R21.2, U14.1
unnamed: C37.1, FB3.2, L8.1
unnamed: C38.1, U14.2
unnamed: C38.2, U9.1
unnamed: C39.1, U15.2
unnamed: C39.2, U1.1
unnamed: C35.1, D3.1 (K), L8.2
unnamed: FL1.2, J2.1 (In)
unnamed: J3.1 (In), R21.1
unnamed: C7.2, U4.2 (CHPF)
unnamed: C8.1, U4.5 (CLPF)
unnamed: C13.1, U4.14 (INHI)
unnamed: C14.2, U4.15 (INLO)
unnamed: R4.1, U4.7 (VSET)
unnamed: C36.1, FB3.1, R20.2, U6.1 (-)
unnamed: U7.2 (P0), U8.1 (D0)
unnamed: U7.3 (P1), U8.24 (D1)
unnamed: U7.4 (P2), U8.23 (D2)
unnamed: U7.5 (P3), U8.22 (D3)
unnamed: U7.7 (P4), U8.21 (D4)
unnamed: U7.8 (P5), U8.20 (D5)
unnamed: U7.9 (P6), U8.19 (D6)
unnamed: R2.2, U7.10 (P7), U8.16 (LE)
unnamed: C22.1, U8.5 (RF1)
unnamed: C30.2, U8.14 (RF2)

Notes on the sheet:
U4p3
20dB tap to RF detector
I2C Bus Expander To make atten I2C controlled
100 V/V
ADDR - 0b0100000
U4p10
RF Detector Temp Compensation VTGT = 1.4 TCM1 = 0.5 TCM2 = 0.9
VMODE low for Parallel
3-Pole Maximally-Flat 1dB BW 0.7-2G

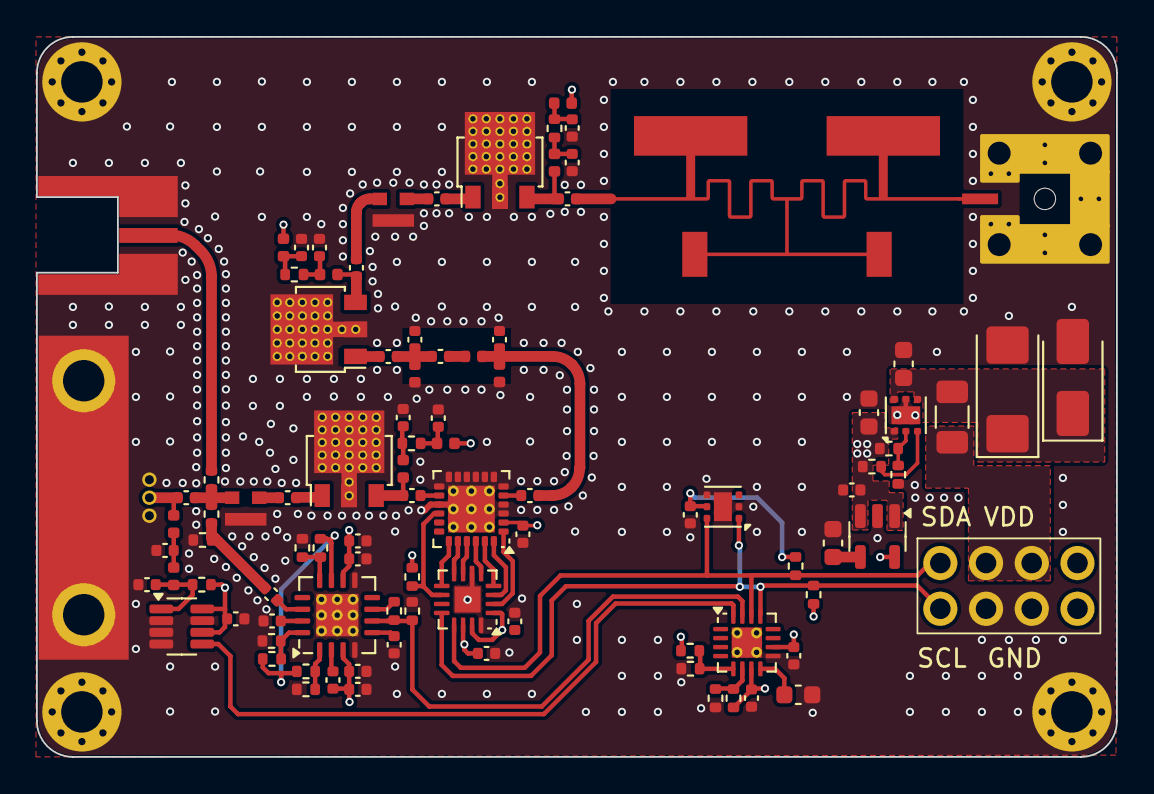
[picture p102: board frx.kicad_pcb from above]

Board: 4 copper layers, 60.0 x 40.0 mm, 100 parts (0 on the bottom side), 60 nets.

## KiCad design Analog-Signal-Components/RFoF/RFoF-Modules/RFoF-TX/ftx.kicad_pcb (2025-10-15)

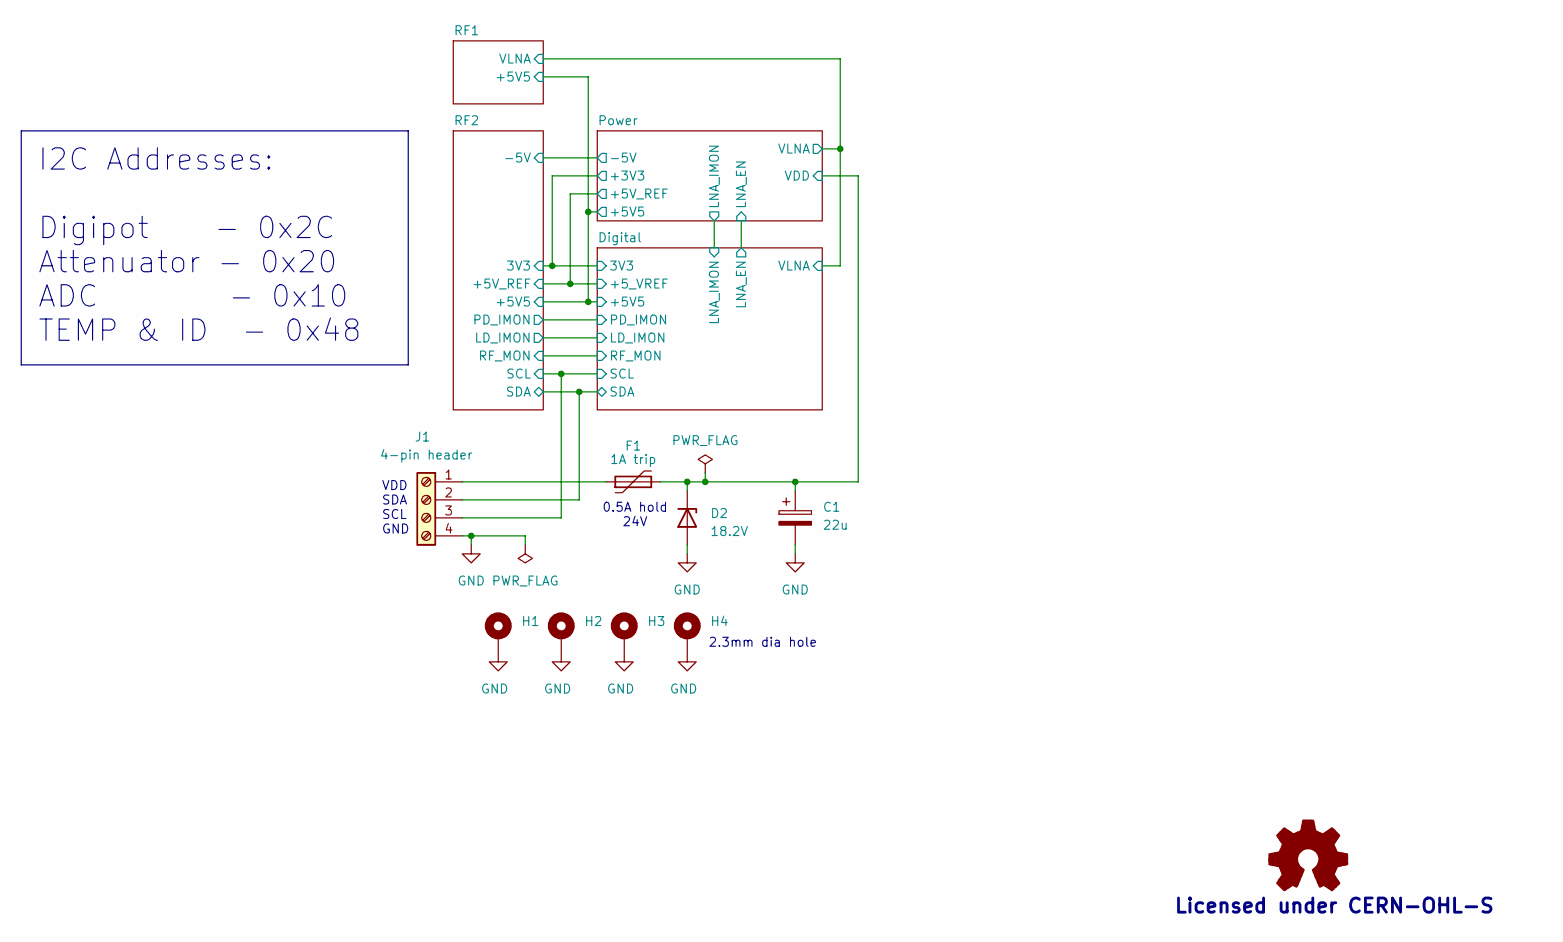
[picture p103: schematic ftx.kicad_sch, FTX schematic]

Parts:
C1: 22u; CP_EIA-6032-28_Kemet-C; MPN 293D226X9025C2TE3
D2: 18.2V; D_SMA; MPN SMAJ11A
F1: 1A trip; Fuse_1206_3216Metric; MPN 1206L050/24WR
H1, H2, H3, H4: MountingHole_Pad; MountingHole_2_Pad_Via
J1: 4-pin header; JST_PH_S4B-PH-SM4-TB_1x04-1MP_P2.00mm_Horizontal; MPN S4B-PH-SM4-TB

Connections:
/Digital/SCL: J1.3; also elsewhere on the board
/Digital/SDA: J1.2; also elsewhere on the board
/Power/VDD: C1.1, D2.1 (K), F1.2; also elsewhere on the board
GND: C1.2, D2.2 (A), H1.1, H2.1, H3.1, H4.1, J1.4; also elsewhere on the board
unnamed: F1.1, J1.1

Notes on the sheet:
VDD SDA SCL GND
Licensed under CERN-OHL-S
0.5A hold 24V
2.3mm dia hole
I2C Addresses: Digipot - 0x2C Attenuator - 0x20 ADC - 0x10 TEMP & ID - 0x48

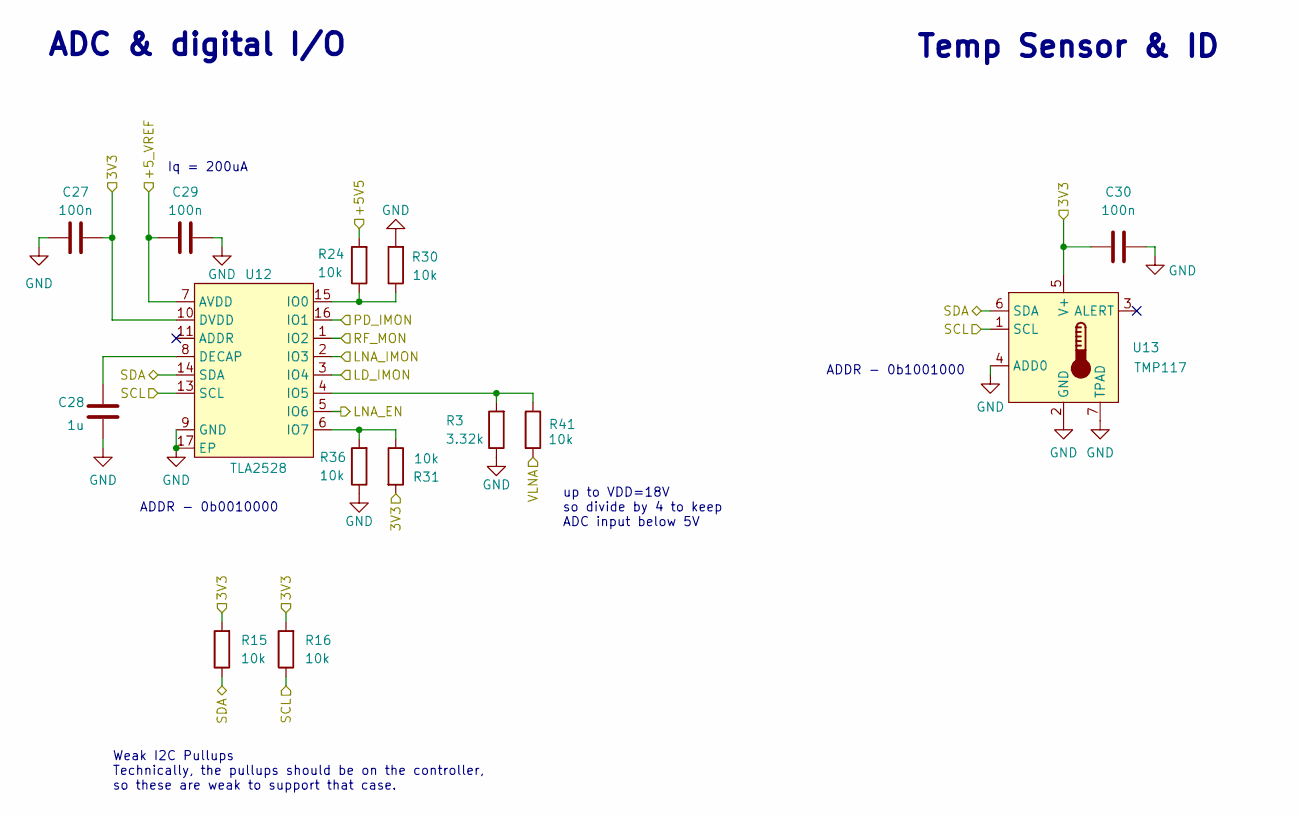
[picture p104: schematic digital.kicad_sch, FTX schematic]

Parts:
C27, C29, C30: 100n; C_0402_1005Metric; MPN CL05B104KP5NNNC
C28: 1u; C_0603_1608Metric; MPN CL10A105KA8NNNC
R3: 3.32k; R_0402_1005Metric; MPN RC0402FR-073K32L
R15, R16, R24, R30, R31, R36, R41: 10k; R_0402_1005Metric; MPN RC0402FR-0710KL
U12: TLA2528; WQFN-16-1EP_3x3mm_P0.5mm_EP1.68x1.68mm_LargeThermalVias; MPN TLA2528IRTER
U13: TMP117; WSON-6-1EP_2x2mm_P0.65mm_EP1x1.6mm; MPN TMP117AIDRV

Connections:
/Digital/3V3: C27.2, C30.2, R15.2, R16.2, R31.2, U12.10 (DVDD), U13.5 (V+); also elsewhere on the board
/Digital/+5V5: R24.2; also elsewhere on the board
/Digital/+5_VREF: C29.2, U12.7 (AVDD); also elsewhere on the board
/Digital/LD_IMON: U12.3 (IO4); also elsewhere on the board
/Digital/LNA_EN: U12.5 (IO6); also elsewhere on the board
/Digital/LNA_IMON: U12.2 (IO3); also elsewhere on the board
/Digital/PD_IMON: U12.16 (IO1); also elsewhere on the board
/Digital/RF_MON: U12.1 (IO2); also elsewhere on the board
/Digital/SCL: R16.1, U12.13 (SCL), U13.1 (SCL); also elsewhere on the board
/Digital/SDA: R15.1, U12.14 (SDA), U13.6 (SDA); also elsewhere on the board
/Digital/VLNA: R41.2; also elsewhere on the board
GND: C27.1, C28.2, C29.1, C30.1, R3.1, R30.2, R36.1, U12.9 (GND), U12.17 (EP), U13.2 (GND), U13.4 (ADD0), U13.7 (TPAD); also elsewhere on the board
unnamed: C28.1, U12.8 (DECAP)
unnamed: R24.1, R30.1, U12.15 (IO0)
unnamed: R3.2, R41.1, U12.4 (IO5)
unnamed: R31.1, R36.2, U12.6 (IO7)

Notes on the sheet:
Weak I2C Pullups Technically, the pullups should be on the controller, so these are weak to support that case.
ADDR - 0b1001000
Iq = 200uA
up to VDD=18V so divide by 4 to keep ADC input below 5V
ADDR - 0b0010000
Temp Sensor & ID
ADC & digital I/O

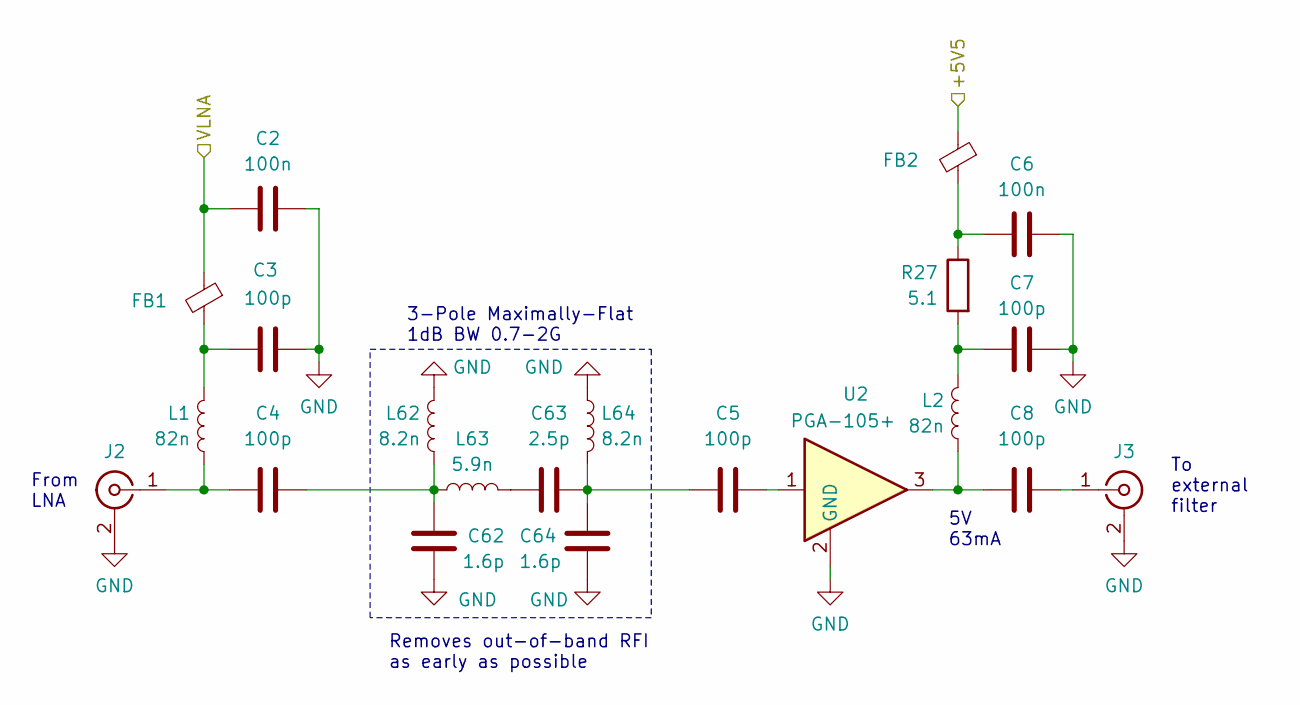
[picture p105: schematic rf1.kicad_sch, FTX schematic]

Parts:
C2, C6: 100n; C_0402_1005Metric; MPN CL05B104KP5NNNC
C3, C4, C5, C7, C8: 100p; C_0402_1005Metric; MPN CBR04C101J3GAC
C62, C64: 1.6p; C_0402_1005Metric; MPN GJM1555C1H1R6WB01D
C63: 2.5p; C_0402_1005Metric; MPN GJM1555C1H2R5WB01D
FB1, FB2: BLM15PG100SN1D; L_0402_1005Metric; MPN BLM15PG100SN1D
J2, J3: Conn_Coaxial; SMA_4Layer; MPN DL-SMA-K513-08K
L1, L2: 82n; L_0402_1005Metric; MPN LQW15AN82NG00D
L62, L64: 8.2n; L_0402_1005Metric; MPN LQW15AN8N2G00D
L63: 5.9n; L_0402_1005Metric; MPN LQW15AN5N9B80D
R27: 5.1; R_0402_1005Metric; MPN ERJ-2GEJ5R1X
U2: PGA-105+; SOT89-HighTemp; MPN PGA-105+

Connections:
/Digital/+5V5: FB2.1; also elsewhere on the board
/Digital/VLNA: C2.1, FB1.1; also elsewhere on the board
GND: C2.2, C3.2, C6.2, C7.2, C62.2, C64.2, J2.2 (Ext), J3.2 (Ext), L62.1, L64.1, U2.2 (GND); also elsewhere on the board
unnamed: C3.1, FB1.2, L1.1
unnamed: C4.2, C62.1, L62.2, L63.1
unnamed: C5.1, C63.2, C64.1, L64.2
unnamed: C5.2, U2.1
unnamed: C6.1, FB2.2, R27.1
unnamed: C7.1, L2.1, R27.2
unnamed: C8.1, L2.2, U2.3
unnamed: C63.1, L63.2
unnamed: C4.1, J2.1 (In), L1.2
unnamed: C8.2, J3.1 (In)

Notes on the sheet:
5V 63mA
From LNA
To external filter
Removes out-of-band RFI as early as possible
3-Pole Maximally-Flat 1dB BW 0.7-2G

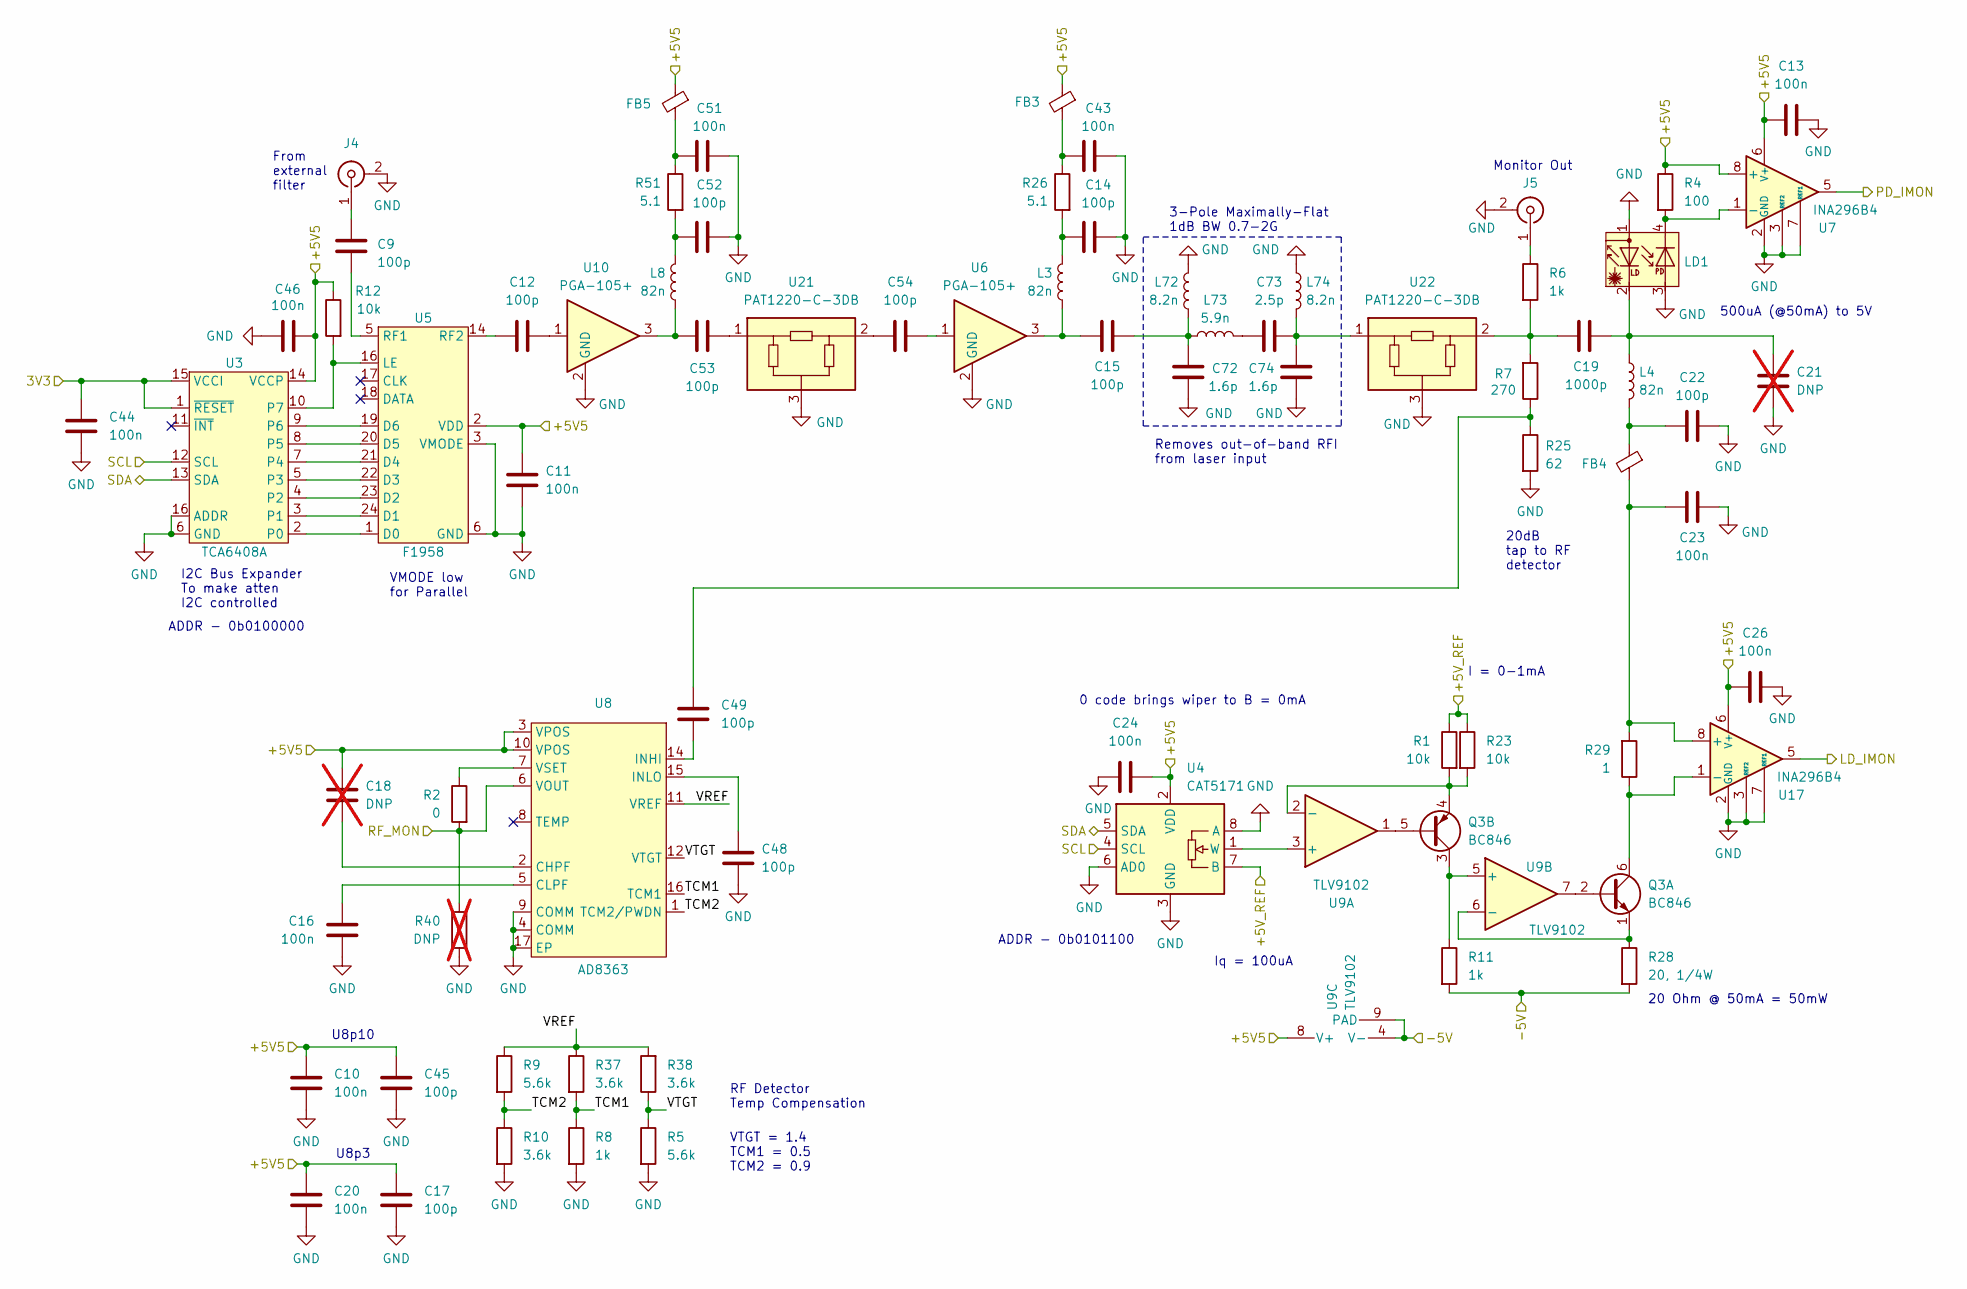
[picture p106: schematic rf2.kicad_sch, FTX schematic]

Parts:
C9, C12, C14, C15, C17, C22, C45, C48, C49, C52, C53, C54: 100p; C_0402_1005Metric; MPN CBR04C101J3GAC
C10, C11, C13, C16, C20, C23, C24, C26, C43, C44, C46, C51: 100n; C_0402_1005Metric; MPN CL05B104KP5NNNC
C18, C21: DNP; C_0402_1005Metric; not fitted
C19: 1000p; C_0402_1005Metric; MPN C0402C102J3GAC7867
C72, C74: 1.6p; C_0402_1005Metric; MPN GJM1555C1H1R6WB01D
C73: 2.5p; C_0402_1005Metric; MPN GJM1555C1H2R5WB01D
FB3, FB4, FB5: BLM15PG100SN1D; L_0402_1005Metric; MPN BLM15PG100SN1D
J4: Conn_Coaxial; SMA_4Layer; MPN DL-SMA-K513-08K
J5: Conn_Coaxial; SMA_4Layer; MPN DL-SMA-KS13-08K
L3, L4, L8: 82n; L_0402_1005Metric; MPN LQW15AN82NG00D
L72, L74: 8.2n; L_0402_1005Metric; MPN LQW15AN8N2G00D
L73: 5.9n; L_0402_1005Metric; MPN LQW15AN5N9B80D
LD1: LaserDiodeWithBlock; MPN PLMR3-A-1-5-S
Q3: BC846; SOT-363_SC-70-6; MPN BC846BPDW1T1G
R1, R12, R23: 10k; R_0402_1005Metric; MPN RC0402FR-0710KL
R2: 0; R_0402_1005Metric; MPN RC0402FR-070RL
R4: 100; R_0402_1005Metric; MPN RC0402FR-07100RL
R5, R9: 5.6k; R_0402_1005Metric; MPN RC0402FR-075K6L
R6, R8, R11: 1k; R_0402_1005Metric; MPN RC0402FR-071KL
R7: 270; R_0402_1005Metric; MPN RC0402FR-07270RL
R10, R37, R38: 3.6k; R_0402_1005Metric; MPN RC0402FR-073K6L
R25: 62; R_0402_1005Metric; MPN RC0402FR-0762RL
R26, R51: 5.1; R_0402_1005Metric; MPN ERJ-2GEJ5R1X
R28: 20, 1/4W; R_1206_3216Metric; MPN RC1206FR-0720RL
R29: 1; R_0402_1005Metric; MPN RC0402FR-071RL
R40: DNP; R_0402_1005Metric; not fitted
U3: TCA6408A; QFN-16-1EP_3x3mm_P0.5mm_EP1.45x1.45mm; MPN TCA6408ARGTR
U4: CAT5171; SOT-23-8; MPN CAT5171TBI-50GT3
U5: F1958; TQFN-24-1EP_4x4mm_P0.5mm_EP2.6x2.6mm_ThermalVias; MPN F1958NBGK
U6, U10: PGA-105+; SOT89-HighTemp; MPN PGA-105+
U7, U17: INA296B4; SOT-23-8; MPN INA296B4IDDFR
U8: AD8363; Analog_LFCSP-16-1EP_4x4mm_P0.65mm_EP2.35x2.35mm_ThermalVias; MPN AD8363ACPZ-R7
U9: TLV9102; WSON-8-1EP_2x2mm_P0.5mm_EP0.9x1.6mm; MPN TLV9102IDSGR
U21, U22: PAT1220-C-3DB; RF_Attenuator_Susumu_PAT1220; MPN PAT1220-C-3DB-T5

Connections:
/Digital/3V3: C44.1, U3.1 (~RESET), U3.15 (VCCI); also elsewhere on the board
/Digital/+5V5: C10.1, C11.1, C13.2, C17.2, C18.1, C20.1, C24.1, C26.2, C45.2, C46.1, FB3.1, FB5.1, R4.1, R12.1, U3.14 (VCCP), U4.2 (VDD), U5.2 (VDD), U7.6 (V+), U7.8 (+), U8.3 (VPOS), U8.10 (VPOS), U9.8 (V+), U17.6 (V+); also elsewhere on the board
/Digital/+5_VREF: R1.1, R23.1, U4.7 (B); also elsewhere on the board
/Digital/LD_IMON: U17.5; also elsewhere on the board
/Digital/PD_IMON: U7.5; also elsewhere on the board
/Digital/RF_MON: R2.2, R40.1, U8.6 (VOUT); also elsewhere on the board
/Digital/SCL: U3.12 (SCL), U4.4 (SCL); also elsewhere on the board
/Digital/SDA: U3.13 (SDA), U4.5 (SDA); also elsewhere on the board
/Power/-5V: R11.2, R28.2, U9.4 (V-), U9.9 (PAD); also elsewhere on the board
/RF2/TCM1: R8.1, R37.2, U8.16 (TCM1)
/RF2/TCM2: R9.2, R10.1, U8.1 (TCM2/PWDN)
/RF2/VREF: R9.1, R37.1, R38.2, U8.11 (VREF)
/RF2/VTGT: R5.1, R38.1, U8.12 (VTGT)
GND: C10.2, C11.2, C13.1, C14.2, C16.2, C17.1, C20.2, C21.2, C22.2, C23.2, C24.2, C26.1, C43.2, C44.2, C45.1, C46.2, C48.1, C51.2, C52.2, C72.2, C74.2, J4.2 (Ext), J5.2 (Ext), L72.1, L74.1, LD1.1, LD1.3, R5.2, R8.2, R10.2, R25.2, R40.2, U3.6 (GND), U3.16 (ADDR), U3.17 (GND), U4.3 (GND), U4.6 (AD0), U4.8 (A), U5.3 (VMODE), U5.4 (GND), U5.6 (GND), U5.7 (GND), U5.8 (GND), U5.9 (GND), U5.10 (GND), U5.11 (GND), U5.12 (GND), U5.13 (GND), U5.15 (GND), U5.25 (GND), U6.2 (GND), U7.2 (GND), U7.3 (REF2), U7.4 (GND), U7.7 (REF1), U8.4 (COMM), U8.9 (COMM), U8.17 (EP), U10.2 (GND), U17.2 (GND), U17.3 (REF2), U17.4 (GND), U17.7 (REF1), U21.3, U22.3; also elsewhere on the board
unnamed: C12.2, U10.1
unnamed: C14.1, L3.1, R26.2
unnamed: C15.1, L3.2, U6.3
unnamed: C15.2, C72.1, L72.2, L73.1
unnamed: C19.1, C21.1, L4.1, LD1.2
unnamed: C19.2, R6.2, R7.2, U22.2
unnamed: C22.1, FB4.1, L4.2
unnamed: C43.1, FB3.2, R26.1
unnamed: C49.1, R7.1, R25.1
unnamed: C51.1, FB5.2, R51.1
unnamed: C52.1, L8.1, R51.2
unnamed: C53.1, L8.2, U10.3
unnamed: C53.2, U21.1
unnamed: C54.1, U21.2
unnamed: C54.2, U6.1
unnamed: C73.1, L73.2
unnamed: C73.2, C74.1, L74.2, U22.1
unnamed: C9.1, J4.1 (In)
unnamed: J5.1 (In), R6.1
unnamed: Q3.2 (B1), U9.7
unnamed: Q3.6 (C1), R29.1, U17.1 (-)
unnamed: Q3.1 (E1), R28.1, U9.6 (-)
unnamed: Q3.5 (B2), U9.1
unnamed: Q3.3 (C2), R11.1, U9.5 (+)
unnamed: Q3.4 (E2), R1.2, R23.2, U9.2 (-)
unnamed: U3.2 (P0), U5.1 (D0)
unnamed: U3.3 (P1), U5.24 (D1)
unnamed: U3.4 (P2), U5.23 (D2)
unnamed: U3.5 (P3), U5.22 (D3)
unnamed: U3.7 (P4), U5.21 (D4)
unnamed: U3.8 (P5), U5.20 (D5)
unnamed: U3.9 (P6), U5.19 (D6)
unnamed: R12.2, U3.10 (P7), U5.16 (LE)
unnamed: U4.1 (W), U9.3 (+)
unnamed: C9.2, U5.5 (RF1)
unnamed: C12.1, U5.14 (RF2)
unnamed: LD1.4, R4.2, U7.1 (-)
unnamed: C18.2, U8.2 (CHPF)
unnamed: C16.1, U8.5 (CLPF)
unnamed: C49.2, U8.14 (INHI)
unnamed: C48.2, U8.15 (INLO)
unnamed: R2.1, U8.7 (VSET)
unnamed: C23.1, FB4.2, R29.2, U17.8 (+)

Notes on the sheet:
3-Pole Maximally-Flat 1dB BW 0.7-2G
I = 0-1mA
20dB tap to RF detector
0 code brings wiper to B = 0mA
Monitor Out
ADDR - 0b0100000
Removes out-of-band RFI from laser input
RF Detector Temp Compensation
ADDR - 0b0101100
U8p10
500uA (@50mA) to 5V
U8p3
Iq = 100uA
VMODE low for Parallel
20 Ohm @ 50mA = 50mW
I2C Bus Expander To make atten I2C controlled
VTGT = 1.4 TCM1 = 0.5 TCM2 = 0.9
From external filter

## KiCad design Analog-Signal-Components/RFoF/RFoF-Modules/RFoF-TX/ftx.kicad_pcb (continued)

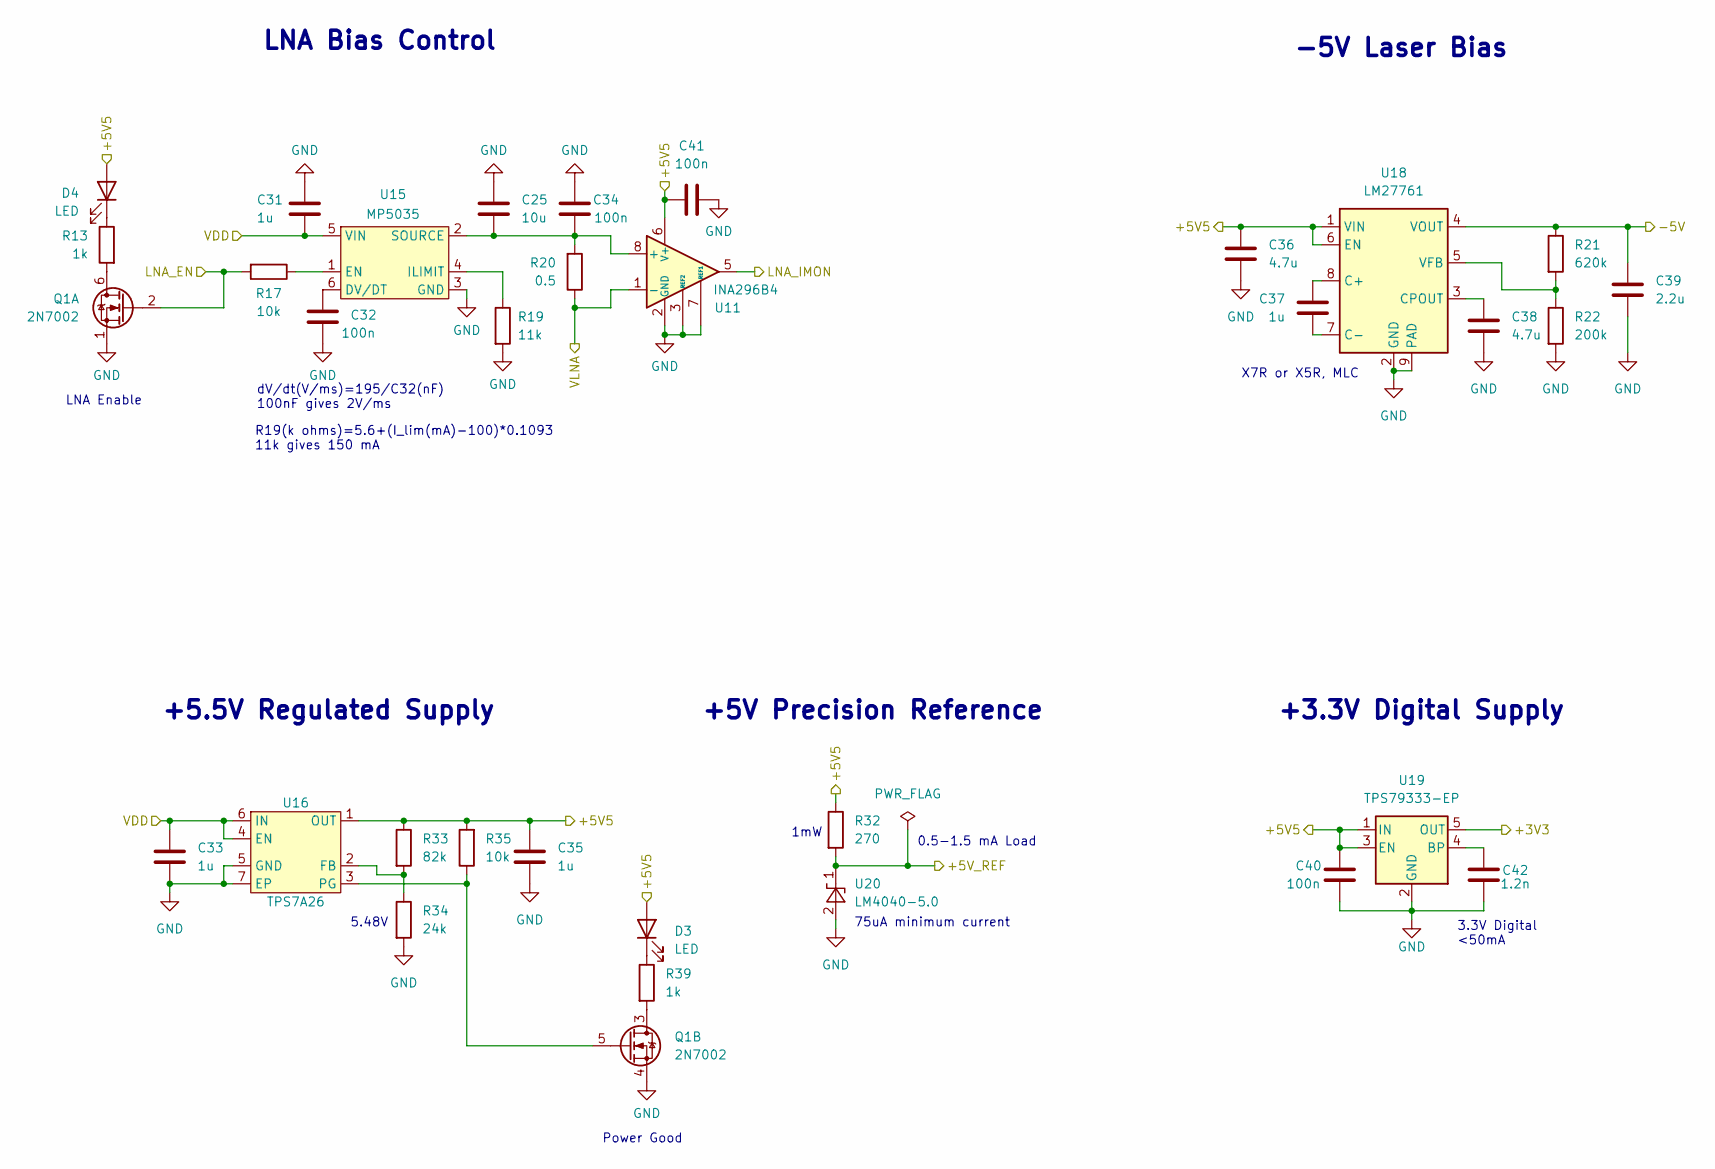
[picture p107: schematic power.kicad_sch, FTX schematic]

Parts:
C25: 10u; C_0603_1608Metric; MPN CL10A106MA8NRNC
C31, C33, C35, C37: 1u; C_0603_1608Metric; MPN CL10A105KA8NNNC
C32, C34, C40, C41: 100n; C_0402_1005Metric; MPN CL05B104KP5NNNC
C36, C38: 4.7u; C_0603_1608Metric; MPN CL10A475KP8NNNC
C39: 2.2u; C_0603_1608Metric; MPN CL10A225KP8NNNC
C42: 1.2n; C_0603_1608Metric; MPN GCM1885C1H122JA16D
D3, D4: LED; LED_0603_1608Metric; MPN LTST-C193KRKT-5A
Q1: 2N7002; SOT-363_SC-70-6; MPN 2N7002DW
R13, R39: 1k; R_0402_1005Metric; MPN RC0402FR-071KL
R17, R35: 10k; R_0402_1005Metric; MPN RC0402FR-0710KL
R19: 11k; R_0402_1005Metric; MPN RC0402FR-0711KL
R20: 0.5; R_0603_1608Metric; MPN RL0603FR-070R5L
R21: 620k; R_0402_1005Metric; MPN RC0402FR-07620KL
R22: 200k; R_0402_1005Metric; MPN RC0402FR-07200KL
R32: 270; R_0402_1005Metric; MPN RC0402FR-07270RL
R33: 82k; R_0402_1005Metric; MPN RC0402FR-0782KL
R34: 24k; R_0402_1005Metric; MPN RC0402FR-0724KL
U11: INA296B4; SOT-23-8; MPN INA296B4IDDFR
U15: MP5035; TSOT-23-6; MPN MP5035GJ-Z
U16: TPS7A26; WSON-6-1EP_2x2mm_P0.65mm_EP1x1.6mm; MPN TPS7A2601DRVR
U18: LM27761; WSON-8-1EP_2x2mm_P0.5mm_EP0.9x1.6mm; MPN LM27761DSGR
U19: TPS79333-EP; SOT-23-5; MPN TPS79333DBVREP
U20: LM4040-5.0; SOT-23; MPN LM4040CYM3-5.0-TR

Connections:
/Digital/3V3: U19.5 (OUT); also elsewhere on the board
/Digital/+5V5: C35.1, C36.1, C40.1, C41.2, D3.2 (A), D4.2 (A), R32.1, R33.1, R35.2, U11.6 (V+), U16.1 (OUT), U18.1 (VIN), U18.6 (EN), U19.1 (IN), U19.3 (EN); also elsewhere on the board
/Digital/+5_VREF: R32.2, U20.1 (K); also elsewhere on the board
/Digital/LNA_EN: Q1.2 (G), R17.2; also elsewhere on the board
/Digital/LNA_IMON: U11.5; also elsewhere on the board
/Digital/VLNA: R20.1, U11.1 (-); also elsewhere on the board
/Power/-5V: C39.1, R21.1, U18.4 (VOUT); also elsewhere on the board
/Power/VDD: C31.2, C33.1, U15.5 (VIN), U16.4 (EN), U16.6 (IN); also elsewhere on the board
GND: C25.1, C31.1, C32.2, C33.2, C34.1, C35.2, C36.2, C38.2, C39.2, C40.2, C41.1, C42.1, Q1.1 (S), Q1.4 (S), R19.2, R22.2, R34.2, U11.2 (GND), U11.3 (REF2), U11.4 (GND), U11.7 (REF1), U15.3 (GND), U16.5 (GND), U16.7 (EP), U18.2 (GND), U18.9 (PAD), U19.2 (GND), U20.2 (A); also elsewhere on the board
unnamed: D3.1 (K), R39.1
unnamed: D4.1 (K), R13.1
unnamed: Q1.6 (D), R13.2
unnamed: Q1.3 (D), R39.2
unnamed: Q1.5 (G), R35.1, U16.3 (PG)
unnamed: C25.2, C34.2, R20.2, U11.8 (+), U15.2 (SOURCE)
unnamed: C32.1, U15.6 (DV/DT)
unnamed: R17.1, U15.1 (EN)
unnamed: R19.1, U15.4 (ILIMIT)
unnamed: R33.2, R34.1, U16.2 (FB)
unnamed: C37.1, U18.8 (C+)
unnamed: C37.2, U18.7 (C-)
unnamed: C38.1, U18.3 (CPOUT)
unnamed: R21.2, R22.1, U18.5 (VFB)
unnamed: C42.2, U19.4 (BP)

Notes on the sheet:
dV/dt(V/ms)=195/C32(nF) 100nF gives 2V/ms
R19(k ohms)=5.6+(I_lim(mA)-100)*0.1093 11k gives 150 mA
1mW
+5V Precision Reference
-5V Laser Bias
3.3V Digital <50mA
0.5-1.5 mA Load
LNA Enable
Power Good
+3.3V Digital Supply
5.48V
75uA minimum current
X7R or X5R, MLC
+5.5V Regulated Supply
LNA Bias Control

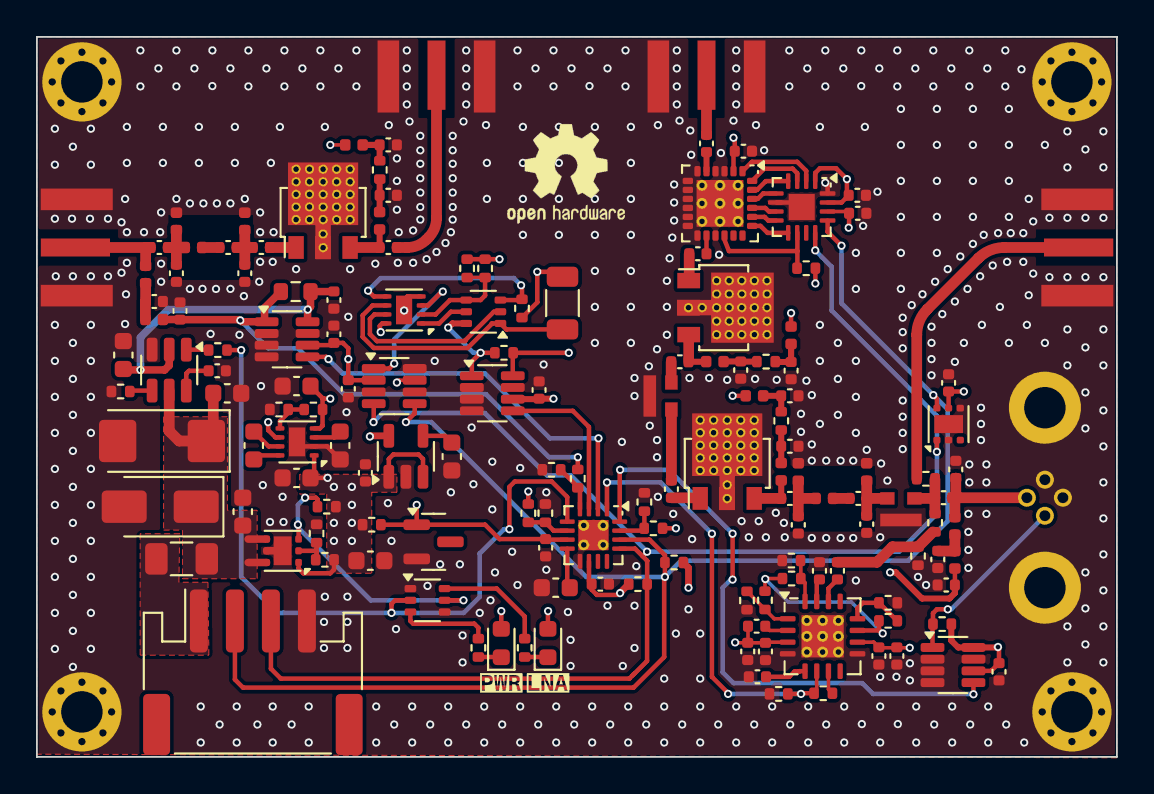
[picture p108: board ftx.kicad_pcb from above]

Board: 4 copper layers, 60.0 x 40.0 mm, 152 parts (0 on the bottom side), 91 nets.

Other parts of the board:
kibuzzard-65317E70: G***; kibuzzard-65317E70
kibuzzard-65317EA1: G***; kibuzzard-65317EA1

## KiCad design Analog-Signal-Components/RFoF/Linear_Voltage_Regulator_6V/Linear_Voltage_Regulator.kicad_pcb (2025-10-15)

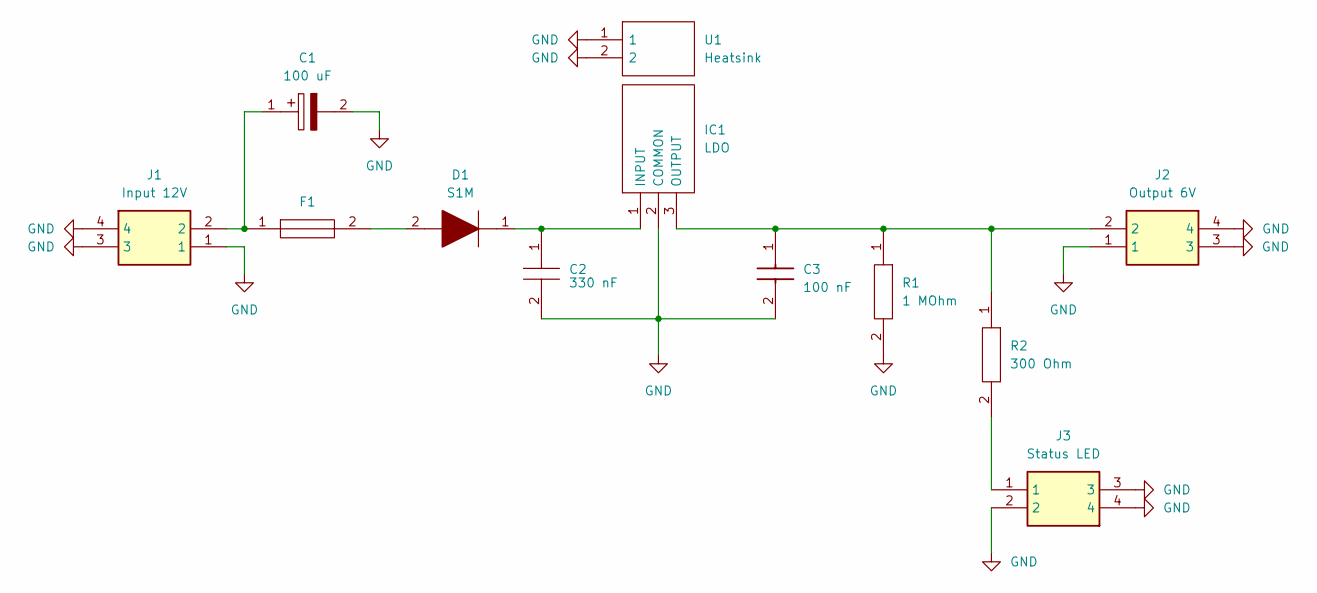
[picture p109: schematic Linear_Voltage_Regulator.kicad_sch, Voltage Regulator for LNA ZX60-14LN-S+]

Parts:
C1: 100 uF; T491X; Mouser Part Number 80-T491X107K025AT
C2: 330 nF; CAPC2012X100N; Mouser Part Number 81-GRM21AR72A334KA5L
C3: 100 nF; CAPC2012X140N
D1: S1M; DIOM5227X270N; Mouser Part Number 512-S1M
F1: 0154001.DRT; Mouser Part Number 576-0154001.DRT
IC1: LDO; TO254P460X1010X1720-3P; Mouser Part Number 755-BA17806CP-E2
J1: Input 12V; 43650-02YY_091011; Mouser Part Number 538-43650-0211
J2: Output 6V; 43650-02YY_091011; Mouser Part Number 538-43650-0211
J3: Status LED; 43650-02YY_091011; Mouser Part Number 538-43650-0211
R1: 1 MOhm; ERA6AEB101V; Mouser Part Number 667-ERA-6AEB105V
R2: 300 Ohm; ERJS1T_U1T__2512_; Mouser Part Number 667-ERJ-U1TF2000U
U1: Heatsink; 513002B02500G; Mouser Part Number 532-513002B25G

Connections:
GND: C1.2, C2.2, C3.2, IC1.2 (COMMON), J1.1, J1.3, J1.4, J2.1, J2.3, J2.4, J3.2, J3.3, J3.4, R1.2, U1.1, U1.2
unnamed: C1.1, F1.1, J1.2
unnamed: D1.2, F1.2
unnamed: C2.1, D1.1, IC1.1 (INPUT)
unnamed: C3.1, IC1.3 (OUTPUT), J2.2, R1.1, R2.1
unnamed: J3.1, R2.2


Board: 2 copper layers, 55.0 x 58.0 mm, 12 parts (0 on the bottom side), 6 nets.

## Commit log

2019-03-14 Updated latest additions by Matt
    [30-24-300 A PAX Case assembly.SLDASM, 30-24-310-A Case Box assembly.SLDASM, 30-24-311-A Case, Box.SLDPRT, 30-24-312-A Case Support bar.SLDPRT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]
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2019-05-20 Adding parts lists
    [RFCB_bckback(1029)_partslist.xls, RFCB_pwr(1025)_partslist.xls]
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2019-05-20 Parts lists.
    [14.6GHZ_6way_1017_partslist.xls, 16-26Ghz _6way_1014c_partslist.xls]
2019-05-21 Initial upload
    [Appendix A.xls]
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2020-09-23 Added the LNA data sheets for all Antonio Feeds
    [LNF LNA Shipments .xlsx]
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2020-10-30 Adding maps.
    [Datapoints-20-B.xls, Datapoints.csv, Datatpoints with elevation.dwg, Drawing1.dwg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]
2020-11-23 Added Antonio Feed Documentation
    [-002 X1 noise HC.csv, -002 Y1 noise HC.csv, -004 Noise Testing Record Sheet .xlsx, -004 X1 noise.csv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]
2020-12-03 updated HCRO Time Standard
    [FeedPartsInventory.xlsx]
2020-12-11 Wire Harness Update
    [Control Board to Cryo Board.xlsx, Control to Diaphragm.xlsx, List of materials (24v).xlsx, List of materials (48v).xlsx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]
2020-12-24 updated feed inventory
    [FeedPartsInventory.xlsx]
2021-01-06 updated files antonio feed
    [-004 Noise Testing Record Sheet .xlsx, -004 X1 noise.csv, -004 X2 Noise HC.csv, -004 Y1 noise.csv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]
2021-01-06 added Tsys measurement 3c 2b
    [XC30.csv, XC31.csv, XH30.csv, XH31.csv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]
2021-01-07 added HVAC heat load calculation
    [FeedPartsInventory.xlsx, Heat-Load-Calculation.xlsx]
2021-01-11 added site plan
    [FeedPartsInventory.xlsx, Heat-Load-Calculation.xlsx]
2021-01-16 uploaded meeting slides
    [FeedPartsInventory.xlsx]
2021-01-21 updated network drawing WAN
    [FeedPartsInventory.xlsx]
2021-02-18 updated feed status
    [FeedPartsInventory.xlsx]
2021-02-24 updated Tsys measurements
    [FeedPartsInventory.xlsx, XC01.csv, XC1.csv, XC11.csv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]
2021-03-23 updated antonio feed files
    [-002 X1 noise HC.csv, -002 Y1 noise HC.csv, -004 Noise Testing Record Sheet .xlsx, -004 X1 noise.csv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]
2021-03-23 Added Antenna CAD model
    [1 inch standoff.SLDPRT, 10-32 1-2 Phillips 91772A829.SLDPRT, 1041h.DRL, 1041h.gtl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]
2021-03-25 updated FeedPartsInventory
    [FeedPartsInventory.xlsx, __FeedPartsInventory.xlsx]
2021-03-25 added PAM design files
    [BTM-COP.GBR, CascadedTsysATA-with-slope-new.xlsx, NoRESwd7.csv, OptimizationSetup1_Profile1.csv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]
2021-03-30 Attemplifier Tests
    [Attemplifier Test.xlsx]
2021-04-15 added balun files
    [2xbalun_box.xls, Feed3Dwbalun.dwg, GES11.csv, GES11_2.csv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]
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2021-04-22 updated meeting slides
    [Wiring purchase 3.31.2021.xlsx, __FeedPartsInventory.xlsx]
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2021-05-03 added PAX measurements
    [1041h.DRL, 1041h.gtl, 1041h.gto, 1041h_drill_gerber.gbr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]
2021-05-06 updated feed parts
    [XC1.csv, XH1.csv, YC1.csv, YH1.csv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]
2021-05-07 added LNA measurements
    [__FeedPartsInventory.xlsx]
2021-05-11 Control board wire harness directions
    [List of materials (rainbow).xlsx]
2021-05-11 24v wire harness directions
    [List of materials (24v).xlsx]
2021-05-18 added LO files
    [10MHZ-TEST-LO2-ALL-CLK.csv, 10MHZ-TEST-LO2-NO-SNAP-RACK.csv, 10MHZ-TEST-LOA-ALL-CLK.csv, 10MHZ-TEST-LOA-CLK.csv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]
2021-05-18 added LNA bias supply files
    [LNF-PS_2_parts_list_for_distribution-CJC_rev17.xlsx, PAXController.brd, PAXController.drl, ip2022block.SLDPRT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]
2021-05-18 added 2C measurement
    [XC1.csv, XC2.csv, XH1.csv, XH2.csv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]
2021-05-19 Wire harness Updates
    [List of materials (24v).xlsx, List of materials (48v).xlsx, List of materials (extra long single clam).xlsx, List of materials (fan).xlsx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]
2021-05-26 Tsys measurements
    [XC1.csv, XC2.csv, XH1.csv, XH2.csv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]
2021-06-02 added 2h Tsys measurement
    [XC01.csv, XC1.csv, XC11.csv, XC12.csv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]
2021-06-03 updated feed parts inventory
    [__FeedPartsInventory.xlsx]
2021-06-21 updates slides
    [__FeedPartsInventory.xlsx]
2021-06-24 added meeting slides
    [XC1.csv, XC10.csv, XH1.csv, XH10.csv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]
2021-06-28 LNA Datasheet updates
    [-002 X1 noise HC.csv, -002 Y1 noise HC.csv, -004 Noise Testing Record Sheet .xlsx, -004 X1 noise.csv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]
2021-06-28 Finishing LNA Datasheets
    [XC01.csv, XC1.csv, XC10.csv, XC11.csv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]
2021-06-29 Update feed base data sheets
    [__FeedPartsInventory.xlsx]
2021-06-30 added feed wiring document
    [24 Wiring Harness Purchase List.xlsx]
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2021-07-09 PAX updates
    [__FeedPartsInventory.xlsx]
2021-07-15 updates meeting presentation
    [24 Wiring Harness Purchase List copy.xlsx, CascadedTsysATA-IAF.xls, CascadedTsysATA.xls, Wiring Purchase 6.30.2021.xlsx]
2021-08-05 added drive box files
    [Accelnet module.SLDPRT, AzElDriveBoard.SLDASM, AzElDriveBoard.SLDDRW, AzElDriveBoard.SLDPRT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]
2021-08-11 Signal Processing AC Diagrams
    [__FeedPartsInventory.xlsx]
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2021-08-13 Main distribution
    [XC1.csv, XH1.csv, YC1.csv, YH1.csv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]
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2021-08-26 added new meeting slides
    [Heat-Load-Calculation.xlsx, XC1.csv, XH1.csv, YC1.csv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]
2021-09-02 update meeting slides and memo
    [__FeedPartsInventory.xlsx]
2021-09-30 updated memo
    [CONTROL_BOARD_ONLY_V3_BOM.xlsx, CONTROL_BOARD_ONLY_V3_BOM_15_BUILD.xlsx, CONTROL_RIM_BOARD_V3.DSN, XC2.csv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]
2021-10-05 added SNAP board enclosure document
    [CascadedTsysATA.xls, XC2.csv, XH2.csv, YC2.csv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]
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2021-10-19 added attemplifer design files
    [1050a.CSV, 1050a.DRL, 1050a.GBL, 1050a.GTL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]
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2021-11-18 added attemplifier memo
    [1050a.CSV, 1050a.DRL, 1050a.GBL, 1050a.GTL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]
2021-11-19 added meeting slide
    [__FeedPartsInventory.xlsx]
2022-01-12 Adding ATA operations brainstorming documents
    [ATA_Operations.xlsx]
2022-01-12 Deleted Operations file to move to correct folder
    [ATA_Operations.xlsx]
2022-01-12 Added Operations brainstorming documents
    [ATA_Operations.xlsx]
2022-01-12 Added row to project list
    [ATA_Operations.xlsx]
2022-01-14 Deleted Excel file in transfer to Google Sheets
    [ATA_Operations.xlsx]
2022-01-14 added meeting presentation
    [CascadedTsysATA.xls, __FeedPartsInventory.xlsx]
2022-01-27 added GRASP Memo
    [1 inch standoff.SLDPRT, 10-32 1-2 Phillips 91772A829.SLDPRT, 3-8 -16 nut 92673A125.SLDPRT, 30-14-225-A Pin Clamp Cap.SLDPRT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]
2022-02-20 added 4e measurement
    [CascadedTsysATA.xls, XC1.csv, XC2.csv, XC3.csv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]
2022-02-21 added direct feed measurement with SA
    [XC10.csv, XC11.csv, XC12.csv, XH10.csv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]
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2022-03-08 Minor wire harness updates
    [List of materials (triple cable).xlsx]
2022-03-23 added LO firmware files
    [XC13.csv, XC14.csv, XC15.csv, XC16.csv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]
2022-03-28 updated Tsys data
    [3C-NF.csv, XC01.csv, XC1.csv, XC10.csv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]
2022-03-28 Add moon tsys measurements
    [1a_Results.csv, 1c_Results.csv, 1e_Results.csv, 1f_Results.csv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]
2022-04-04 added tip-link documents
    [ATA-MEC-105 Tip Arm Link R03.STEP, Antonio Feed Material List.xlsx, Feed Gold Plating.xlsx]
2022-04-12 measured 3c and 4j
    [XC1.csv, XC2.csv, XH1.csv, XH2.csv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]
2022-06-09 updated feed parts document
    [__FeedPartsInventory.xlsx]
2022-06-16 Wiring Updates
    [List of materials (metal block).xlsx]
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2022-09-02 Feed Updates
    [__FeedPartsInventory.xlsx]
2022-09-02 PAX Box updates
    [__FeedPartsInventory.xlsx]
2022-09-15 added Tsys 5e
    [XC1.csv, XC2.csv, XH1.csv, XH2.csv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]
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2022-09-21 added Tsys measurements
    [XC3.csv, XC4.csv, XH3.csv, XH4.csv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]
2022-09-28 added feed info
    [__FeedPartsInventory.xlsx]
2022-09-29 added 48V check column
    [__FeedPartsInventory.xlsx]
2022-10-06 updated feeds
    [Feed -018_X pole_ypam1010_65K_Noise.csv, Feed -018_Y pole_ypam1010_65K_Noise.csv, Feed -019_X pole_ypam1010_69K_Noise.csv, Feed -019_Y pole_ypam1010_69K_Noise.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]
2022-10-24 Wire harness tweeks
    [List of materials (24v).xlsx, List of materials (48v).xlsx, List of materials (red and blue).xlsx]
2022-10-26 Wire Harness COMPLETE
    [List of materials (the monster).xlsx]
2023-02-08 added RFSoC document
    [CascadedTsysATA.xls]
2023-03-14 added building document
    [ATA_PAM.xls]
2024-02-12 added IF mapping
    [Mapping DSP.xlsx, __FeedPartsInventory.xlsx]
2024-02-12 added old labeling document
    [Cable labeling old.xlsx]
2024-02-12 added files for IF Power Splitter
    [24567474_01.ipt, 24567474_02.ipt, 24567474_03.ipt, 24567474_04.ipt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]
2024-02-21 corrected ports in document
    [Mapping DSP.xlsx]
2024-03-04 added manual in MEMOS on how to read raw encoder values
    [Feed Control Commands 6.0.xlsx]
2024-03-05 added feed firmware documentation
    [Feed Control Commands 6.0.xlsx]
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2024-04-05 First draft of GReX EMI measurements
    [Baseline.csv, absorber.csv, baseline.csv, closed.csv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]
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2024-04-12 moved backend config into dsp folder
    [Cable labeling old.xlsx, Mapping DSP.xlsx]
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2024-05-21 Correct length to 25ft for tunning C
    [Mapping DSP.xlsx]
2024-05-23 Minor corrections
    [Mapping DSP.xlsx]
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2024-08-02 added Wrappot Fix PCB and manual
    [ATA_Wrappot_Fix_V1.0.brd, ATA_Wrappot_Fix_V1.0_Part_List.xlsx, copper_bottom.GBL, copper_top.GTL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]
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2025-03-20 fixed a layout problem
    [SEFD-1C.xlsx, SEFD-2H.xlsx]
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2026-02-20 RFoF PCB fixes
    [AlarmSwitch.GBL, AlarmSwitch.GBO, AlarmSwitch.GBP, AlarmSwitch.GBS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]
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
